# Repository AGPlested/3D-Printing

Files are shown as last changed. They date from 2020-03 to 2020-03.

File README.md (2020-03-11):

# 3D-Printing
3D Printable objects used for microscopy and beyond in the Plested lab (www.fmp-berlin.de/plested), Humboldt University and FMP Berlin

Mounts for Princeton Instruments ProEM512 (KP ProEM mount 0.2) and Photometrics Prime95B (KP Prime95B mount 0.2) cameras are included. These cameras have imperial threaded mounting points. The mounts allow the camera to be mounted directly to a M6 tapped 25 mm pitch breadboard, or to standard M6 tapped posts. You will need 8x32 (PI) or 1/4x20 (Photometrics) imperial screws to attach the cameras to mounts. 

On a standard Prusa i3 mk3 3D printer (https://www.prusa3d.com), the KP Prime95B mount 0.2 takes about 12 hours to print, and uses about 3€ of PLA. We use standard settings: 15% fill-in, no supports, 0.15mm layers - in other words, the 'QUALITY MK3' setting. 

The coverslip holder (KP CSH 0.2) is meant to accept 25 mm 1.5H glass coverslips, for example for STORM or TIRF microscopy. We print this with the 0.05mm ULTRADETAIL setting. 

* .scad files are for generating models in openSCAD: https://www.openscad.org
* .stl files are for generating 3D models to print. For example, with Slic3r: https://slic3r.org

Feel free to use these designs for any purpose. Comments and suggestions welcome. 

Twitter: @andrewplested

Email: andrew.plested@hu-berlin.de

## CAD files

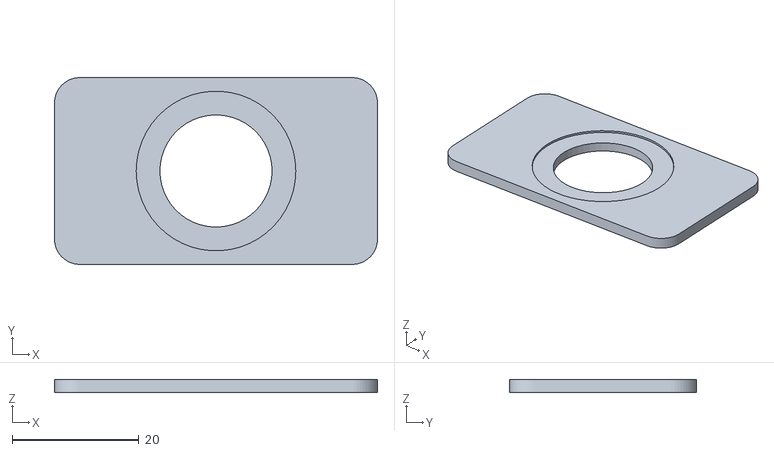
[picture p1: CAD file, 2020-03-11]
KP CSH 0.2.stl
51.0 x 29.5 x 2.00

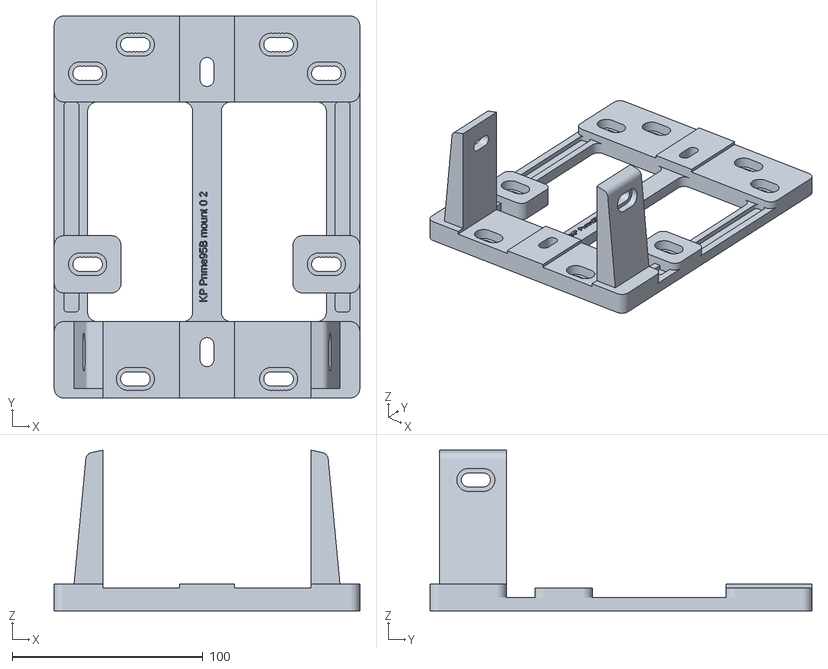
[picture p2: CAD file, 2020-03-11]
KP Prime95B mount 0.2.stl
160.0 x 200.0 x 84.1

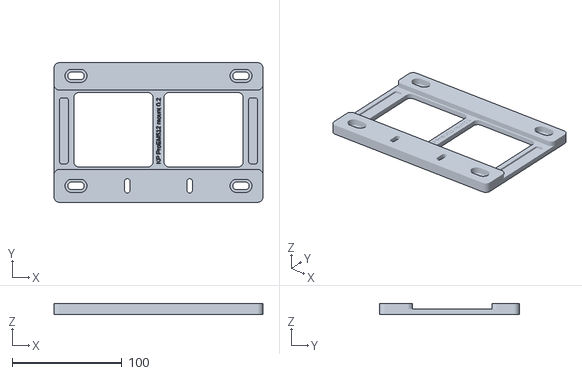
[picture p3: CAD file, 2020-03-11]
KP ProEM 512 mount 0.2.stl
190.0 x 127.0 x 10.0

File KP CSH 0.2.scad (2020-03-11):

difference()
    {
    union()
        {
        translate([4,0,0]) cube([43,29.5,2]);
        translate([0,4,0]) cube([51,21.5,2]);   
        translate([4,4,0]) cylinder(r=4,h=2, $fn=50);
        translate([47,4,0]) cylinder(r=4,h=2, $fn=50);
        translate([4,25.5,0]) cylinder(r=4,h=2, $fn=50);
        translate([47,25.5,0]) cylinder(r=4,h=2, $fn=50);
        }
    translate([25.5,14.75,0]) cylinder(r=8.85,h=2, $fn=50);
    translate([25.5,14.75,1.65]) cylinder(r=12.6,h=0.35, $fn=50);
    translate([8,27,0]) 
        linear_extrude(height = 1) {
            rotate ([0,180,90]){
            text("KP CSH 0.2", size=3, direction = "ltr");
    }       
}
}
    
    

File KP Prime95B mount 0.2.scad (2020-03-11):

// Prime95B mount for Metric 25mm pitch M6 breadboard
// For 39mm high mounting (on 25 mm posts)
// For 3D printer 
// Andrew Plested and Benjamin Koenig, Humboldt University and Leibniz FMP


width = 160;   //x 
depth = 200;   //y along optical axis
thick = 14;    //z thickness of plate
cam_w = 109;   //width of Prime 95B from datasheet + 0.6 mm 
c_r = 5;       //corner radius
aff = thick-2; //affordance over M6 mounting holes

module socket_cap_hole (inner, outer, atx, aty, zthick, cap)
{
    translate([atx, aty, 0]) cylinder(r=inner, h=zthick, $fn=50);
    translate([atx, aty, zthick-cap]) cylinder(r=outer, h=cap, $fn=50);
}

module 1_4_20_cap_hole (atx, aty, zthick)
{
    8_32_cap_diam = 12;
    8_32_cap_thick = 6;
    8_32_clearance = 7.2;
    socket_cap_hole (8_32_clearance / 2, 8_32_cap_diam / 2, atx, aty, zthick, 8_32_cap_thick);
}

module 8_32_cap_hole (atx, aty, zthick)
{
    8_32_cap_diam = 8;
    8_32_cap_thick = 5;
    8_32_clearance = 5;
    socket_cap_hole (8_32_clearance / 2, 8_32_cap_diam / 2, atx, aty, zthick, 8_32_cap_thick);
}    
 
module M6_cap_hole (atx, aty, zthick)
{
    M6_clearance = 7.5;
    M6_cap_thick = 6.5;
    M6_cap_diam = 12;
    socket_cap_hole (M6_clearance / 2, M6_cap_diam / 2, atx, aty, zthick, M6_cap_thick);
}

module rounded_slab (width, depth, c_r, thick)
{
    translate([c_r,0,0]) cube([width-2*c_r, depth, thick]);
    translate([0,c_r,0]) cube([width, depth-2*c_r, thick]);   
    translate([c_r,c_r,0]) cylinder(r=c_r, h=thick, $fn=50);
    translate([width - c_r,c_r,0]) cylinder(r=c_r, h=thick, $fn=50);
    translate([c_r, depth - c_r,0]) cylinder(r=c_r, h=thick, $fn=50);
    translate([width-c_r, depth-c_r, 0]) cylinder(r=c_r, h=thick, $fn=50);    
}

module rounded_side_block (base, top, high, depth)
{
    translate ([0,depth,0])
    rotate ([90,0,0])  
    linear_extrude(height = depth) 
    {
        hull() 
        {
        square (.1);
        translate ([base, 0, 0]) square (.1);
        translate ([0, high, 0]) square (.1);
        translate ([top-5, high-5, 0]) scale([1/50, 1/50, 1/50]) circle (200);
        }
    }
}

difference() 
{
    union()
    {
        difference()
        {
            //frame with central cut-outs
            rounded_slab(width, depth, c_r, thick/2);
            translate([17.5,40,0])   rounded_slab(55, 115, c_r, thick/2);
            translate([87.5,40,0])   rounded_slab(55, 115, c_r, thick/2);    

            //negative beams
            beam = 3;
            translate([5,45,thick/2-beam])   rounded_slab(8, 110, 2, beam); 
            translate([width-13,45,thick/2-beam])   rounded_slab(8, 110, 2, beam);
         
            
            
            //signature  
            translate([80,50,thick/2-2]) 
                linear_extrude(height = 2) 
                {
                    rotate ([0,0,90])
                    {
                        text("KP Prime95B mount 0.2", size=4, direction = "ltr");
                    }       
                }
            }  
        //end bars (union with base frame)
        translate([0, 0, thick/2])   rounded_slab(width, 40, c_r, thick/2);   
        translate([0, 155, thick/2])  rounded_slab(width, 45, c_r, thick/2);  
            
        //mid tabs (union with base frame)
        translate([width-35, 55, 0]) rounded_slab(35, 30, c_r, thick-2); 
        translate([0, 55, 0]) rounded_slab(35, 30, c_r, thick-2); 
            
        //Side mounting (union with base frame)
        translate ([width/2 + cam_w/2, 5, thick]) 
            rounded_side_block (15, 10, 70, 35);
        translate ([width/2 - cam_w/2, 5, thick]) 
            mirror([1,0,0]) rounded_side_block (15, 10, 70, 35);  
        
    }   
    
    // loop to elongate holes
    // 1/4-20 mounting holes facing towards camera (away from baseplate)
    for (i = [0 : 8]){
        translate([width/2, 20+i, thick]) 
            rotate ([0,180,0])   1_4_20_cap_hole (0, 0, thick);
        translate([width/2, 20+146.7+i, thick]) 
            rotate ([0,180,0])   1_4_20_cap_hole (0, 0, thick);
        
     // 1/4-20 transverse mounting holes   
        translate([width/2+cam_w/2, 20+i, thick+cam_w/2]) 
            rotate ([0,90,0])   1_4_20_cap_hole (0, 0, 12);
        translate([width/2-cam_w/2, 20+i, thick+cam_w/2]) 
            rotate ([0,-90,0])   1_4_20_cap_hole (0, 0, 12);   
    }
    
    //affordances subtracted from endbars above M6 cap holes 
    translate([0, 155, aff])   cube([width/2 - cam_w/2 + 40, 45, 2]);   
    translate([width/2 + cam_w/2 - 40, 155, aff])  cube([width - cam_w/2 + 40, 45, 2]); 
    translate([width/2 - cam_w/2, 0, aff])   cube([40, 40, 2]);   
    translate([width/2 + cam_w/2 - 40, 0, aff])  cube([40, 40, 2]); 
    
    //baseplate mounting (M6) 25 mm pitch 
    //loop to elongate holes
    for (i = [0 : 2 : 8]){
        M6_cap_hole(width/2 -41.5 +i, 10, aff);
        M6_cap_hole(width/2 +33.5 +i, 10, aff);
        M6_cap_hole(width/2 -41.5 +i, 185, aff);
        M6_cap_hole(width/2 +33.5 +i, 185, aff);
        M6_cap_hole(width/2 -66.5 +i, 170, aff);
        M6_cap_hole(width/2 +58.5 +i, 170, aff);
        M6_cap_hole(width/2 -66.5 +i, 70, aff);
        M6_cap_hole(width/2 +58.5 +i, 70, aff);

    }
    
}

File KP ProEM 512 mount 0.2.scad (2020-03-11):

// Prototype ProEM 512 mount for Metric 25mm pitch M6 breadboard
// for 3D printer 

width = 190;    //x
depth = 127;    //y
thick = 10;     //z
c_r = 5;       //corner radius

module socket_cap_hole (inner, outer, atx, aty, zthick, cap)
{
    translate([atx, aty, 0]) cylinder(r=inner, h=zthick, $fn=50);
    translate([atx, aty, zthick-cap]) cylinder(r=outer, h=cap, $fn=50);
}

module 8_32_cap_hole (atx, aty, zthick)
{
    8_32_cap_diam = 8;
    8_32_cap_thick = 5;
    8_32_clearance = 5;
    socket_cap_hole (8_32_clearance / 2, 8_32_cap_diam / 2, atx, aty, zthick, 8_32_cap_thick);
}    
 
module M6_cap_hole (atx, aty, zthick)
{
    M6_clearance = 7;
    M6_cap_thick = 6;
    M6_cap_diam = 12;
    socket_cap_hole (M6_clearance / 2, M6_cap_diam / 2, atx, aty, zthick, M6_cap_thick);
}

module rounded_slab (width, depth, c_r, thick)
{
    translate([c_r,0,0]) cube([width-2*c_r, depth, thick]);
    translate([0,c_r,0]) cube([width, depth-2*c_r, thick]);   
    translate([c_r,c_r,0]) cylinder(r=c_r, h=thick, $fn=50);
    translate([width - c_r,c_r,0]) cylinder(r=c_r, h=thick, $fn=50);
    translate([c_r, depth - c_r,0]) cylinder(r=c_r, h=thick, $fn=50);
    translate([width-c_r, depth-c_r, 0]) cylinder(r=c_r, h=thick, $fn=50);    
}

difference() 
{
    union()
    {
        difference()
        {
            //frame with central cut-outs
            rounded_slab(width, depth, c_r, thick/2);
            translate([18,32,0])   rounded_slab(72, 68, c_r, thick/2);
            translate([100,32,0])   rounded_slab(72, 68, c_r, thick/2);    

            //negative beams
            translate([5,35,3])   rounded_slab(8, 60, 2, 2); 
            translate([width-13,35,3])   rounded_slab(8, 60, 2, 2);
        
        
            //signature  
            translate([97,35,3]) 
                linear_extrude(height = 2) 
                {
                    rotate ([0,0,90])
                    {
                        text("KP ProEM512 mount 0.2", size=4, direction = "ltr");
                    }       
                }
            }  
        //end bars (union with base frame)
        translate([0, 0, 5])   rounded_slab(190, 30, c_r, 5);   
        translate([0, 102, 5])  rounded_slab(190, 25, c_r, 5);  
    }   
    
    //8-32 facing towards camera (away from baseplate)
    for (i = [0 : 8]){
        translate([width/2-28.3, 11+i, 10]) rotate ([0,180,0])   8_32_cap_hole (0, 0, 10);
        translate([width/2+28.3, 11+i, 10]) rotate ([0,180,0])   8_32_cap_hole (0, 0, 10);
    }
    
    //baseplate mounting (M6) - check pitch!!!!
    for (i = [0 : 2 : 8]){
        M6_cap_hole(width/2-79+i, 15, 10);
        M6_cap_hole(width/2+71+i, 15, 10);
        M6_cap_hole(width/2-79+i, 115, 10);
        M6_cap_hole(width/2+71+i, 115, 10);
        
    //cutout under distant bar
    translate([35, 107, 0])   rounded_slab(120, 15, c_r, 5); 


    }
    
}

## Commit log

2020-03-11 Camera mounts and coverslip holder added
    [BKAP CSH 0.2.scad, BKAP CSH 0.2.stl, KP Prime95B mount 0.2.scad, KP Prime95B mount 0.2.stl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]
2020-03-11 Changed names
    [KP CSH 0.2.scad, KP CSH 0.2.stl]
